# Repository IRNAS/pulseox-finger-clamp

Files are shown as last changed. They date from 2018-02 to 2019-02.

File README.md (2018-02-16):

## Pulseox Mechanics
This repository contains STL files and assembly instructions.

1. *Instructions* folder contains manufacturing and assembly instructions of finger clamp and device housing
2. *finger-clip* folder contains STL files of the finger clip
3. *housing* folder contains STL files of the device housing

## License

All our projects are as usefully open-source as possible.

Hardware including documentation is licensed under [CERN OHL v.1.2. license](http://www.ohwr.org/licenses/cern-ohl/v1.2)

Firmware and software originating from the project is licensed under [GNU GENERAL PUBLIC LICENSE v3](http://www.gnu.org/licenses/gpl-3.0.en.html).

Open data generated by our projects is licensed under [CC0](https://creativecommons.org/publicdomain/zero/1.0/legalcode).

All our websites and additional documentation are licensed under [Creative Commons Attribution-ShareAlike 4 .0 Unported License] (https://creativecommons.org/licenses/by-sa/4.0/legalcode).

What this means is that you can use hardware, firmware, software and documentation without paying a royalty and knowing that you'll be able to use your version forever. You are also free to make changes but if you share these changes then you have to do so on the same conditions that you enjoy.

Koruza, GoodEnoughCNC and IRNAS are all names and marks of Institut IRNAS Rače. 
You may use these names and terms only to attribute the appropriate entity as required by the Open Licences referred to above. You may not use them in any other way and in particular you may not use them to imply endorsement or authorization of any hardware that you design, make or sell.

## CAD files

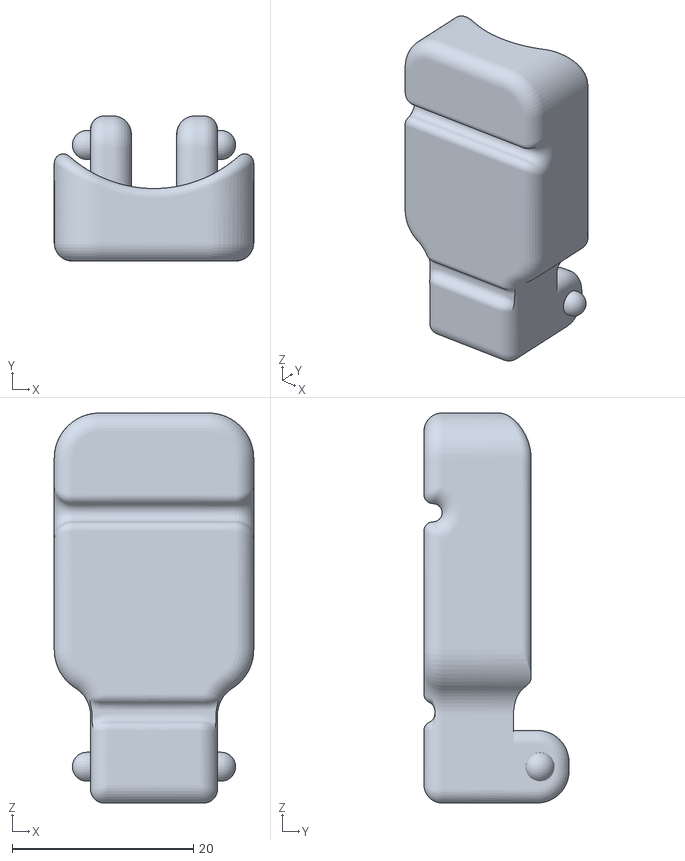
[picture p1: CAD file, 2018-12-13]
finger-clip/probe_in.stl
22.0 x 16.0 x 43.0

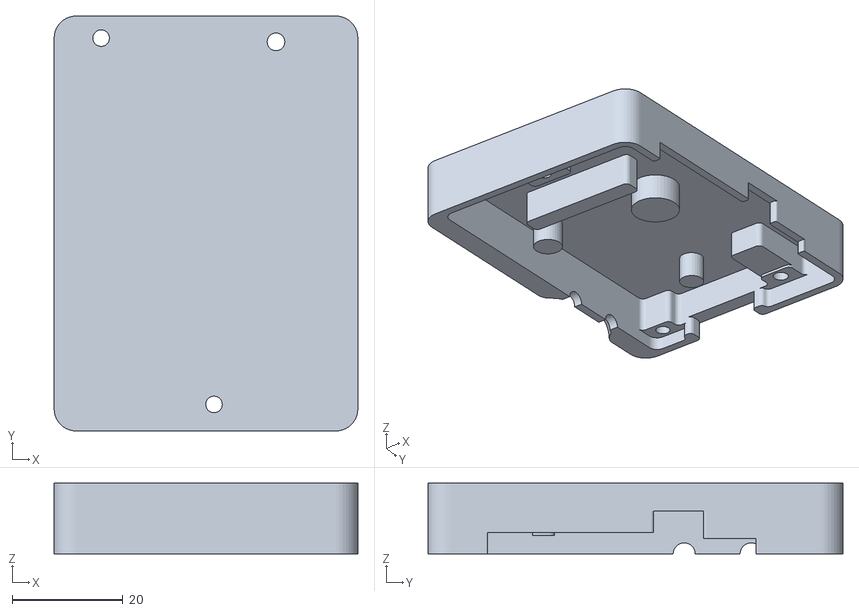
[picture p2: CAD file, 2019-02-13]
housing/housing_bottom.stl
54.9 x 75.0 x 12.8

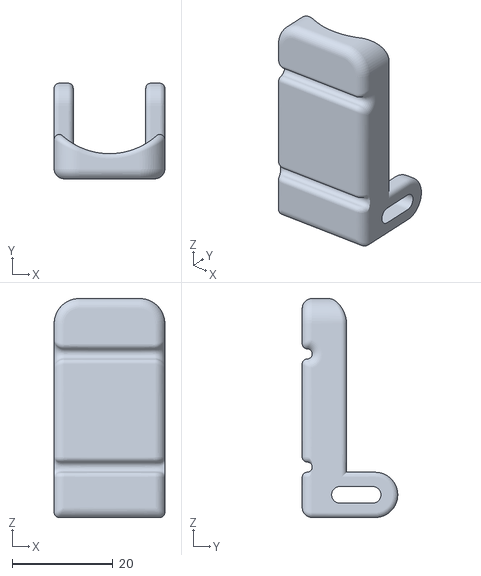
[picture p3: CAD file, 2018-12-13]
finger-clip/probe_out.stl
22.0 x 19.0 x 43.5

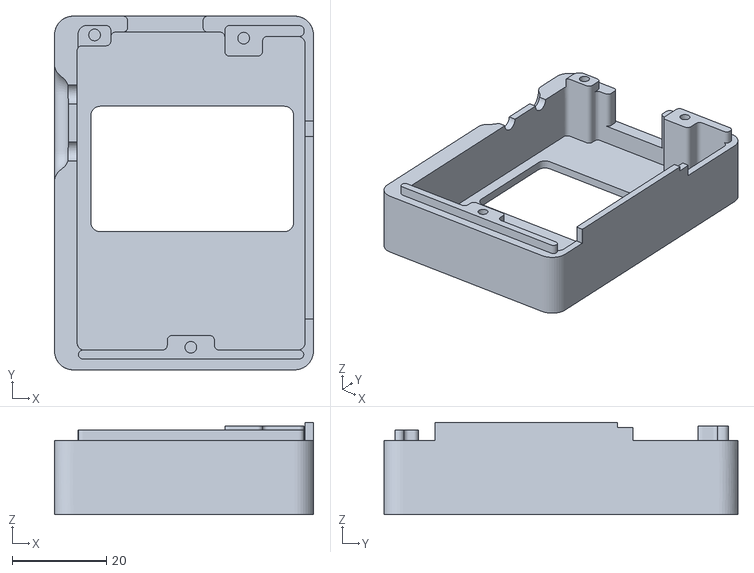
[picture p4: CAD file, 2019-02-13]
housing/housing_lid.stl
54.9 x 75.0 x 19.6

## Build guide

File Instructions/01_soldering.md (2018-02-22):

# Soldering
Once the PCB soldering is complete, the UTP connector must be soldered on to the pins on the main PCB using short wires (the new version will have the UTP connector included on the PCB). For the wire use [IDC 6 wire](http://www.canadarobotix.com/image/cache/data/products/0/44-1-800x800.JPG) without connectors. On one side, crimp on a UTP connector (use middle 6 pins). Peel the wire insulation off on the other side so the wires are ready for soldering.

pinoutmainpcb

 | RECEPTABLE PIN | PCB PIN |
 |------|-------|
 |1| --- |
 |2|LED 3|
 |3|LED 2|
 |4|LED 1|
 |5|3V3|
 |6|RCV|
 |7|GND|
 |8| --- |

pin_asspin_ass

| UTP CON PIN | PCB | PCB PIN |
|------|-------|-------|
|1|---|---|
|2|LED| LED 3 |
|3|LED| LED 2 |
|4|LED| LED 1 |
|5|RECEIVER| RCV |
|6|RECEIVER| 3V3 |
|7|RECEIVER| GND |
|8|---|---|

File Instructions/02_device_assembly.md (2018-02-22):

# Manufacturing and Assembly

## Table of contents
 - [Overview](#OVER)
 - [Part Manufacturing](#MANUFACTURING)
 - [Assembly Brief](#ASSEMBLY)

## 1 Overview and Toolset 
Here you can find manufacturing and assembly details for a single Pulse Oximeter device. Download all the files for 3D printing from this repository. 

- Manufacturing time:
  - 3D printing - 1h
  - soldering (1 unit by hand, depends on the skills) - 2h
- Assembly time: 10min

### 1.2 Tool List
- Screw set:
  - 4 pcs. M2.5x5mm screws DIN7985 or similar
  - 4 pcs. M3x14mm screws DIN965 or similar
  - 2 pcs. M3x10mm screws DIN965 or similar

- Drill set:
  - 2mm drill
  - 2.5mm drill
  - 3mm drill
  - chamfer drill

- Philips screwdriver
- Battery Hand Drill

### 1.4 Parts list

All parts can be found in build_files folder.

Finger clamp:
- probe_in.STL
- probe_out.STL

Case:
- case_bottom.STL
- case_top.STL
- spacer.STL

## 2 Part Manufacturing 

- 3D print all the parts
- Cut/peel away the brim on the parts with a knife or similar
- Hole widening: widen the holes and drill chamfers as marked on the scheme

## 3 Assembly 

**Finger clip**

Collect the necessary parts and tools:

- 3D printed parts (2 parts)
- a kitchen rubber band (2 pcs)
- Superglue
- Transparent nail UV gel
- 2-5mL syringe
- UV lamp

| | DESCRIPTION | STEP | |
|------|------|------|------|
|1.| 3D print both parts (probe_out.stl and probe_in.stl) |step1 | step1 |
|2.| use a little super glue to fixate the LED and sensor PCBs and cables inside the slots | step2a|step2b |
|3.| fill the nail UV gel into the syringe (try to sink the syringe deep enough to prevent the air to enter) |step3a |step3a |
|4.| carefully seal the PCB slots with UV gel, try avoiding air bubbles, be careful not to pu too much gel | step4a| step4b|
|5.| place both parts under the UV lamp for 10 min |step5a |step5b  |
|6.| remove the two parts from the UV lamp and assemble them | step6a | step6b |
|7.| place a rubber band into each of the two outer slots on the finger clip |step7a | step7b|

**Case**

Collect the necessary parts: 3D printed parts, PCB, screws.

step2b

| DESCRIPTION | STEP 1 | STEP 2 |
|------|-------|-------|
|Place the screen into the slot on the case_bottom|step2a|step2b|
|Place the main PCB on the spacer so the connector cables go through the cutout and fix them together with four M2.5x5mm screws|step3a|step3b|
|Place the spacer on the case_bottom over the screen and place the connector in its position before fastening in the two M3x10mm screws on the spacer|step4a|step4b|
|Connect the screen with the main PCB by pulling the slider on the connector out to insert the cable and pushing it back in to lock it in|step5a|step5b|
|Plug in the battery and place the battery next to the spacer.|step6a|step6b|
|Put on the case_top and screw in the four M3x14mm screws|step7a|step7b|

Plug it the UTP cable from the finger clamp into the connector on the case to finish the assembly.
step8a

CONGRATULATIONS! You've assembled your GliaX pulse oximeter. To test if your device works check out [this repository](https://github.com/IRNAS/pulseox-testing).

step8b

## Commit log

2017-07-26 deleted files
    [medic clip v1.SLDPRT, medic clip v1.STL]
2017-07-26 v1
    -too big
    -two joints won't work
    -plastic too thick
    [finger_clamp.SLDPRT, finger_clamp.STL]
2017-07-26 v2
    -right direction (lighter, more practical)
    -drops off finger in horizontal movement (rotation)
    -loop(spring) too big
    -finger doesn't fit further that start of loop
    [finger_clamp.SLDPRT, finger_clamp.STL]
2017-07-26 v3
    -changed design to fit electronics inside
    -smaller loop
    -finger still doesn't fit further than begining of loop
    [finger_clamp.SLDPRT, finger_clamp.STL]
2017-07-26 v4
    -simplified design
    -inside addapts to finger (round shape) to hold it in place
    -hole for sensors on electronics
    [finger_clamp.SLDPRT, finger_clamp.STL]
2017-07-26 v5
    - wider (10mm)
    -smaller loop for beter flexability
    -upper part rounded down at the end to fit better on finger
    [finger_clamp.SLDPRT, finger_clamp.STL]
2017-07-26 v6
    -tried wider (12mm) but it was too wide
    -higher side-walls (rounded inside)
    [finger_clamp.SLDPRT, finger_clamp.STL]
2017-07-26 v7
    -changed width back to 10mm
    [finger_clamp.SLDPRT, finger_clamp.STL]
2017-07-26 v8
    -tried a different loop shape (didn't work out)
    [finger_clamp.SLDPRT, finger_clamp.STL]
2017-07-26 v9
    -changed loop back
    -made side walls on upper and lower part same hight
    -added shape for mounting electronics(test)
    [finger_clamp.SLDPRT, finger_clamp.STL]
2017-07-27 v10
    -started creating a box for the pcb with a top cover
    -two screws to hold the cables
    [finger_clamp.SLDPRT, finger_clamp.STL, finger_clamp_top_cover.SLDPRT, finger_clamp_top_cover.STL]
2017-07-27 v11
    -added third hole for the cover
    [finger_clamp.SLDPRT, finger_clamp.STL, finger_clamp_top_cover.SLDPRT, finger_clamp_top_cover.STL]
2017-07-27 v12
    -tried using the pcb itself as the cover instead of having a 3D printed one
    [finger_clamp.SLDPRT, finger_clamp.STL, finger_clamp_top_cover.SLDPRT, finger_clamp_top_cover.STL]
2017-07-28 upload case v1
    [case.SLDPRT, case.STL]
2017-07-28 upload case v2
    -added hole
    [case.SLDPRT, case.STL]
